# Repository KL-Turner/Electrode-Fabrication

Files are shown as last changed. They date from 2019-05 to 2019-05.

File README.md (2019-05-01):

# Electrode-Fabrication 
Detailed step-by-step instructions for fabrication of Stereotrodes & EMG electrodes

https://kl-turner.github.io/Electrode-Fabrication/

# Materials

| Hardware | Manufacture or Seller | Documentation | Purpose |
| :---                                          | :---                                                                                                         | :---                                                | :--- |
| PFA-Coated Tungsten Wire (795500) | A-M Systems | https://www.a-msystems.com/p-802-pfa-coated-tungsten-wire.aspx | Stereotrode wire |
| Multi-Stranded PFA-Coated Stainless Steel Wire (793200) | A-M Systems | https://www.a-msystems.com/p-806-multi-stranded-pfa-coated-stainless-steel-wire.aspx | EMG wire |
| Polyimide Tubing (822200) | A-M Systems | https://www.a-msystems.com/p-219-polyimide-tubing.aspx | Electrode insulator |
| Gold Connector Pins (ED1199-ND) | Digi-Key | https://www.digikey.com/product-detail/en/mill-max-manufacturing-corp/0489-1-15-15-11-27-04-0/ED1199-ND/434154 | Wire to connector contact |
| PELCO® Colloidal Silver, 30g (16031) | TED PELLA | https://www.tedpella.com/SEMmisc_html/SEMpaint.htm#16031 | Wire to pin conductor | 
| Heat-Shrink Tubing (7496K82) | McMaster-Carr | https://www.mcmaster.com/7496k82 | Electrode insulator | 
| 300 General Purpose Cyanoacrylate (30002) | Vibra-Tite | https://www.vibra-tite.com/adhesives-bonding/vibra-tite-300-general-purpose-cyanoacrylate/ | Electrode strength, solidifcation |
| Gold Pin Headers | Mouser Electronics | https://www.mouser.com/ProductDetail/harwin/m52-5002545/?qs=ulE8k0yEMYYCoPI98NE5xg%3D%3D&countrycode=US&currencycode=USD | Electrode fabrication, protection |

# Equipment

| Hardware | Manufacture or Seller | Documentation | Purpose |
| :---                                          | :---                                                                                                         | :---                                                | :--- |
| Fine Scissors - Tungsten Carbide (14568-12) | Fine Science Tools (FST) | https://www.finescience.com/en-US/Products/Scissors/Standard-Scissors/Fine-Scissors-Tungsten-Carbide/14568-12 | Cut electrode wire(s) |
| Dumont #5 Forceps (11251-20) | Fine Science Tools (FST) | https://www.finescience.com/en-US/Products/Forceps-Hemostats/Dumont-Forceps/Dumont-5-Forceps/11251-20 | Wire stripping, handling |
| Student Standard Pattern Forceps (91100-16) | Fine Science Tools (FST) | https://www.finescience.com/en-US/Products/Student-Instruments/Student-Forceps/Student-Standard-Pattern-Forceps/91100-16 | Handling pins, electrodes |
| M22520/2-01 Miniature Adjustable Indent Crimp Tool | Daniels Manufacturing Corporation (DMC) | https://www.dmctools.com/detail/286 | Crimp pins/wires |
| Light Microscope (general) | Olympus | https://www.olympus-lifescience.com/en/microscopes/ | Simplifies fabrication |
| Helping Hands (any) | Amazon | https://www.amazon.com/SE-MZ101B-Helping-Hand-Magnifier/dp/B000RB38X8/ref=sr_1_4?keywords=helping+hands&qid=1556684628&s=gateway&sr=8-4 | Hold headers during glue drying |
| Electrode Impredence Tester (IMP-2A) | MicroProbes for Life Sciences | https://microprobes.com/products/neuroscience-research-equipment/impedance-testers | Impedence meter |

Other: ruler, razor blades, standard office scissors, any kind of tape, wire/solder for test equipment, NaCl, beaker, Parafilm, coffee, etc etc.

# Instructions

The following instructions outline the step-by-step process for fabricating tungsten stereotrodes and seven-strand stainless steel EMG electrodes.

- **[A]** Unravel a small amount of the desired wire. I typically use ~ 1 inch (25 mm) as it makes handling the wire significantly easier.

- **[B]** Gather as many pieces of wire as you would like, the number of wires (N) is equal to N/2 electrodes. I typically make 20+ wire + pins before assembling the electrodes. You want to your wires to be as straight as possible throughout the entire process, so discard any wire at the end of the spool that is irreparably bent.

- **[C]** Use a pair of fine-tip forceps to strip ~ 3 mm of the Teflon coating off **one** end of each wire. It does not matter which side. You want to strip off just enough coating so that the bare end fits fully into the gold pin, but does not extend significally past the end of the opening. Careful when stripping stranded wire, as you do not want to separate the strands.

| [A] Cutting wire | [B] 2 wires per electrode| [C] Stripping off coating |
|:----:|:----:|:----:|
|  |  |  |

- **[D]** Shake the bottle of colloidal silver (CS) very well. The CS is electrically conductive, allowing current to pass from the wire to the pin. It starts off as a liquid, but quickly dries leaving the conductive particles. Gather up your stripped wires, some gold pins, and a crimper tool. It's nice to work in a well-ventilated area under a fume extractor swing-arm, ventilation table, or fume hood.

- **[E]** Hold a gold pin with the forceps and apply a *small* amount of CS to the opening. It helps to use the brush to lightly work the CS liquid into the pin hole.

- **[F]** Insert the stripped end of the wire into the gold pin opening. I do this by holding the wire vertically and placing the gold pin upside down on top of the wire. 

- **[G]** Set the forceps down and pick up the crimping tool. Still holding the wire vertically with the gold pin balancing on top, insert the gold pin into the crimping tool and crimp the pin 2-3 times. When finished, gently tug the wire to ensure that it is secure. If the wire comes out, toss the pin and try again with a new one. If the wire is secure but the gold pin is severely cracked open or fragile, pull out the wire and re-do it. The last thing you want is a fragile gold pin breaking in half after you've already completed a successful surgery and have the animal is ready to be imaged. *Speaking from experience.*

- **[H]** Repeat the process until you've collected at least twice as many completed wire + pins as the number of electrodes you desire. As mentioned before, I typically make dozens of these at once. Often times I make several dozen on slow days and keep them in a labeled container for later assembly. Be sure to label the container(s), as the stainless steal and tungesten wires look nearly identical unless under a microscope.

| [D] CS and crimpers | [E] Apply CS to gold pin | [F] Insert wire into pin | [G] Crimp gold pin | [H] Repeat as necessary |
|:----:|:----:|:----:|:----:|:----:|
|  |  |  |  |  |

### The remaining steps are easier when done under a microscope, but can be done without one.

|  |
|:----:|
| **Using a microscope makes fabrication significantly easier** |

- **[I]** Cut the polyimide (PI) tubing into the appropriate lengths. For each tungsten stereotrode, I cut two pieces - one at 1 mm in length, and the other at 3 mm in length. For each EMG electrode, I cut two pieces - both 3 mm in length. Careful when cutting the tubing, as it tends to go flying after cut with a razor blade.

- **[J],[K]** While cutting the PI tubing, I find it extremely useful to adhere the small pieces to a piece of tape. This not only prevents the small, static-clinging pieces from sticking to your forceps and gloves, it stabilizes them for easy wire-insertion.

- **[L]** Use the forceps to insert two tungsten wires first into a single 1 mm piece of PI tubing. This can be extremely frustrating to do by eye, but is incredibly easy when using a microscope with just a small amount of magnification. The fit of the two wires inside the tubing will be tight. For EMG electrodes, insert one single wire into a single piece of 3 mm tubing. The fit for these wires will be very loose, but they serve an important purpose discussed later.

- **[M]** Lightly lift the tape and slide the PI tubing further down the wires so that it doesn't slip off. For the tungsten stereotrodes, insert the tips into a second piece of 3 mm tubing. After doing this, remove the wires/tubing from the tape.

| [I] Measure PI tubing | [J] Cut tubing to length | [K] Apply pieces to tape | [L] Insert wires into tubing | [M] Insert into second tubing for stereotrodes |
|:----:|:----:|:----:|:----:|:----:|
|  |  |  |  |  |

- **[N]** Cut equal pieces (to the # of wires) of heat-shrink tubing of approximately equal length. Anywhere between 3-5 mm is fine. I shoot for around 4 mm, but don't actually measure these when cutting as you learn rather quickly what is too short/long by eye. I cut several pieces at once into a container, and then fish out two of approximately equal length for each individual electrode. The tubing serves to physically separate the two gold pins from shorting the circuit.

- **[O]** Gather your parts, as the electrodes are ready to assemble. EMG wires will be separate, stereotrode wires will be together.

- **[P]** Slide a piece of heat-shrink tubing onto each wire. For the EMG wires, this can be done before or after putting the pins into the headers. For the stereotrode wires, you need to put the tubing on first from the pin-side. You made need to slide the pieces of PI tubing back towards the top of the wires to separate the two wires. Be sure to **not bend** the tungsten wires.

- **[Q]** Insert the gold pins into headers. Use a pair of larger (not fine) forceps to do this, as it may require a little bit of *gentle* force. For this example, I have just a single pair of headers per electrode. When I make mine, I typically make 5 electrodes at once and have several electrodes spaced along a single 24-pin header. After the pins are inserted, use a pair of forceps to slide the pieces of heat-shrink tubing to the desired position (See photo). You want the tubing to slightly extend past the top of the gold pin.

- **[R]** Use a heat gun to shrink the tubing. Do not overheat the tubing, it only needs to be heated to the point that it shrinks to its final OD. If you do overheat the electrode, you risk melting and deforming the Teflon coating and the PI tubing. This makes moving the PI tubing during the finishing steps difficult to impossible.

| [N] Cut shrink tubing | [O] Parts ready to assemble | [P] Tubing on pins | [Q] Pins into headers | [R] Heat shrink tubing |
|:----:|:----:|:----:|:----:|:----:|
|  |  |  |  |  |

- **[S]** To finish up the EMG electrodes, align the electrode vertically in the helping hands. Slide the two pieces of PI tubing down as far as they will comfortably go. Ideally, they go all the way past the heat-shrunk tubing and stop at the end of the crimped gold pin. Do not worry if the two pieces are slightly uneven in length. The purpose of these long pieces of PI tubing on the single EMG wires is provide a little bit of reinforcement against the torsional forces on the wire connection during electrode implantation. The stainless steel wires are very flexible, and are typically bent/curved into the muscles during implantation. This PI tubing helps prevent the base of the wire connection from flexing too much and breaking. Unlike the EMG wires, the tungsten stereotrode wires are never bent, and are already inherently very stiff.

- **[T]** Apply a small amount of cyanoacrylate glue to the vertical EMG electrode. You want to get the glue inside the PI tubing and down inside the heat-shrunk tubing. Remember that this tubing is very loose without the glue, so in order for it to serve its purpose, this needs to be let to dry for 30-60 minutes. Careful not to apply too much glue that it drips down the side of the electrode. If the glue drops down and gets inside the pin/header connection, you will unlikely be able to remove the electrode from the header without destroying it.

- **[U]** After the "bottom" of the electrode is dry, flip it over and apply a light, even layer of glue over the entire electrode. You want to get glue on the top of the heat-shrunk tubing (it is not electrically conductive and will not short the pins), all along the sides, and can allow a small amount to drip back down to the portion already glued. Use a Kim-wipe or paper towel to dab away any excess amount at the bottom. The glue serves to secure the two gold pins together, which until now are really only being held together by the actual header, which will be removed upon data acquision.

- **[V]** For the tungsten stereotrodes, there is a bit of a finicky step that makes a world of difference during electrode implantation and data quality. This step can be easy or an absolute pain depending on the electrode, but is nonetheless incredibly important. You want the stereotrode wires to remain parallel to each other as you slide the smaller 1 mm piece of PI tubing towards the base. Naturally, the wires will want to cross each other the further down the electrode you slide the tubing. The tubing is not meant to go *all the way* down (See photo), but should be as far down as possible so that the height of the electrode off the mouse's head is not excessive. The easiest way to do this step is under the microscope with a pair of dedicated "glue" forceps. The longer piece of PI tubing is meant to be kept towards the top of the wire and serves to help keep them together/aligned. Use the forceps to gently squeeze the wires together, but do not puncture the Teflon coating or you risk shorting. If the wires persistently cross each other as you slide down the PI tubing down, use the glue up and down along the length of the top of the wire where the 3 mm PI tubing is. Make sure the wires are straight before doing this, as there is no going back afterwards. The glue will seap inside the PI tubing and after 30-60 seconds create modest adhesion to keep the wires straight. Do not get any on the smaller piece yet. After a brief wait, now gently slide the forceps up and down along the drying glue (re-apply more as necessary) and slide the smaller piece of PI tubing down with glue along your forceps. The wires should be less resistant to crossing at this point due to the glue on the top PI tubing, but will still require patience. Every time the wires cross, move the tubing back up, gently squeeze the wires together to straighten them, and slide the tubing back down. Over minute(s) as the glue dries, you should reach a point where the tubing is getting more difficult to slide up/down, but the wires *should* be better staying together. This is tedious, however, if you can keep the wires straight it will drastically improve your results. If you let the wires cross, they almost *always* separate from each other by several millimeters, either immediately or during trimming. While the (crossed) wires may appear to be glued together straight, the outward forces from the crossing causes the wire tips to separate as soon as the wires are trimmed to the shorter length and the long piece of PI tubing is removed. In my experience, 25% of electrodes require no extra work and are perfectly straight. 50% require a small amount of work little-to-no extra glue to get the wires straight. 25% are a 4-5 minute pain, but maybe one electrode in ten (total) just being tossed at this point due to the inability to prevent the wires from crossing. The benefits of having perfectly straight, parallel electrodes are reduced damage to the brain during implantation and improved localized data due to the tips being closer together. If the tips are separating during implantation, they typically end up several millimeters apart once in their final position.

- **[W]** If you made it this far and have survived (or given up) keeping the wires from crossing, flip the electrode over and apply the thin layer of glue identical to the EMG electrode outlined in **[U]**. For the stereotrodes, I prefer to allow a decent amount of glue to drop down to the bottom creating a sort of upside-down triangle from the heat-shrunk tubing down to the small piece of PI tubing. When it dries, this extra glue provides a noticeable amount of stability to the base of the electrode wires that helps prevent them from bending.

| [S] Align EMG veritcally | [T] Glue PI tubing on top | [U] Flip and glue rest of EMG | [V] Straighten stereotrode wires | [W] Flip and glue rest of stereotrode|
|:----:|:----:|:----:|:----:|:----:|
|  |  |  |  |  |

Allow the electrodes to dry overnight. After they are dry, the wires can be trimmed to the desired length.

# Testing Electrode Impredence
Before using the electrode(s) during surgery, it is imperitive to check that each wire has a good electrical connection and that they are not shorted together. We can quickly do this by testing the impedence of each wire. I prefer to not trim the electrode wires to the desired length until the day of the surgery, testing the electrodes before starting.

Remove the necessary adapter wires from the Drew Lab Thorlabs box next to the meter, and plug them in to the MicroProbes impedance tester.

|  |
|:----:|
| **MicroProbes impendance tester** |

Make sure the *REFERENCE* pin is connected to the bath of 3M NaCl, and the *ELECTRODE* pin is connected to your desired electrode. Turn the meter on, and it should automatically jump to the right (max impedence). Depending on application, you can adjust the *RANGE*, but typically 500kΩ is enough for most of our applications. Attach the electrode the header of the adapter cable. If your electrode is already in headers, you can simply connect the headers to the headers on the adapter. It does not significantly change the impedance.

| Testing each wire         | Testing for shorts        | Meter reading  |
|:-------------------------:|:-------------------------:|:--------------:|
|  |  |  |

Test the wire impedance by dipping the electrode tip into the NaCl beaker. The meter reading should move to between 70 and 250 kΩ (@1 kHz) for the tungsten, and around 20-150 kΩ for the stainless steel. After testing one side, flip the headers around and test the other wire. If you do not get a good reading from *either* wire, do not use the electrode. To check for shorts between the two wires, remove the copper clamp from the NaCl beaker and attach it to the exposed header pin. This meter should not move from max - as we do not want current to pass between the two electrodes. If you do get a reading, make sure that there's no wet NaCl shorting the stereotrode tips, as a small amount of the salt water solution will (temporarily) complete the circuit. If the tips are dry and still read an impedance, do not use the electrode.

If you did not remove the headers when testing the electrode: remove it once before surgery to ensure that no glue got inside the header, as this will make it nearly impossible to remove for data acquisition. Keeping the header on to test the impedence is fine, but it should be removed when recording data. The header to pin connection is tight (which is what is used to connet to the differential amplifier), but the head to header connection is not, and will lead to bad data especially during running/movement events regardless of how stable the stereotax is. Keep the header on during surgical implantation, remove it during imaging, but replace it back on when finished imaging *before* freeing the mouse from the head-bar holder.

**When finished, turn off the meter. Re-cover the NaCl beaker with Parafilm. Put the *ELECTRODE* connectors/wires into the Drew Lab box. The *REFERENCE* connector and copper clamp can stay out and connected to the NaCl beaker.**

For detailed imformation on signal amplification and acquisition, see https://github.com/KL-Turner/LabVIEW-DAQ

For data analysis, check recent publications at https://sites.esm.psu.edu/~pjd17/Drew_Lab/Publications.html

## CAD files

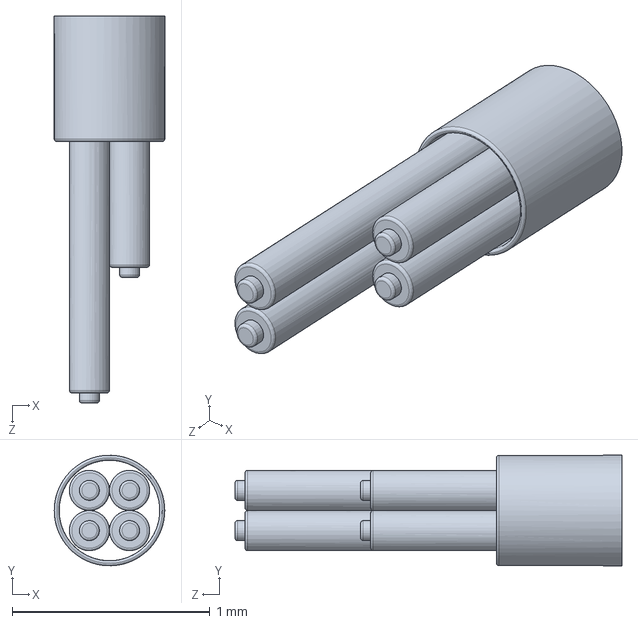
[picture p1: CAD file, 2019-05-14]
4wire_TungstenElectrodes.SLDPRT
0.559 x 0.558 x 1.96 mm

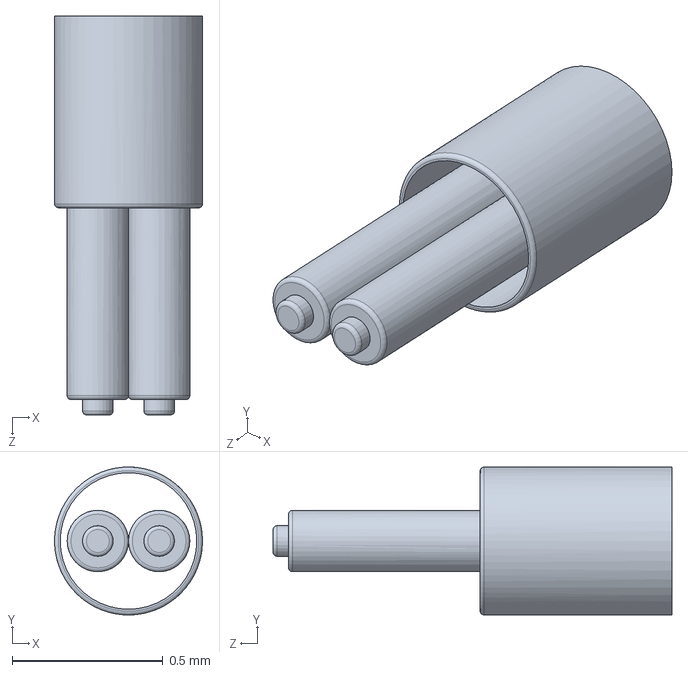
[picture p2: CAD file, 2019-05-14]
2wire_TungstenElectrodes.SLDPRT
0.49 x 0.49 x 1.32 mm
